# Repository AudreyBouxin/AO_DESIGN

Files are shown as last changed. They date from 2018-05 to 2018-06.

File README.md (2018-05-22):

# AO_DESIGN
Here are the codes and simulations for the design of the AO.

The Dimension code shows the calculations made to compute the OAP focal length and distances.

The Zemax file present the current status of the AO design.
The wavelength range is ???
The field of view is 1 arcmin (FoV/2 = 1/2x1/60=0.008333333°) before the dichroic and 8'' ((FoV/2 = 1/2x1/3600=0.00111111°) in the WFS path.

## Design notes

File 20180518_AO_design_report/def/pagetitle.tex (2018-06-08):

\setcounter{page}{1}
%\headsep          = 4.5cm
\fancyhf{}
\fancyhead[C]{
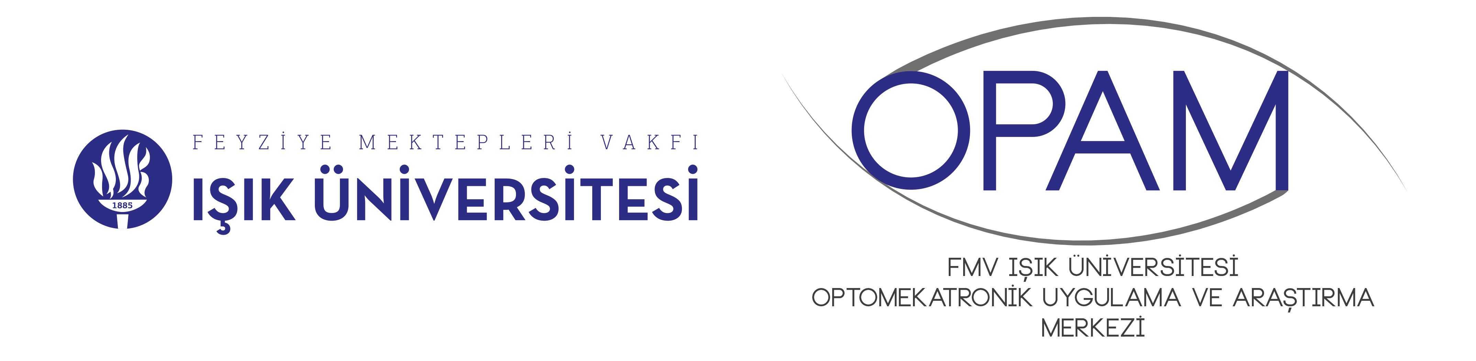
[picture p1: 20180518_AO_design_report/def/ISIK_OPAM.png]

{AO bench design}\hfill {\today}}
\phantom{bla}

\begin{center}
{\LARGE\textbf{AO bench design}} \\
\vspace{2mm}
{\LARGE\textbf{Zemax model and optimization}} \\
\vspace{2mm}
{\LARGE\textbf{post-PDR design}}\\
\end{center}

\begin{center}
\setlength\extrarowheight{20pt}
\begin{tabular}{p{2cm}p{3cm}p{4cm}p{3cm}}
 & Name & Date & Signature\\
Prepared &  A. Bouxin & \today & \begin{minipage}{.2\textwidth}
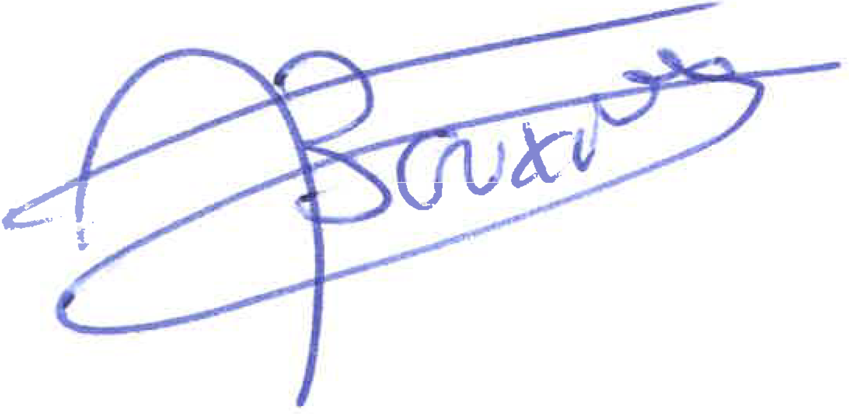
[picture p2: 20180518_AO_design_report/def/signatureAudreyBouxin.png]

\end{minipage} \\
Approved & L. Jolissaint & \today & \begin{minipage}{.2\textwidth}
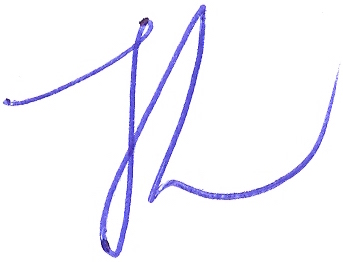
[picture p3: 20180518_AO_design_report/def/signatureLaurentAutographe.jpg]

\end{minipage} \\
& Name & October 10, 2017 & \dotfill \\
Released & Name & \today & \begin{minipage}{.2\textwidth}

\end{minipage} \\
& Name & \today & \dotfill \\
\end{tabular}
\end{center}

\lfoot{\vspace{5mm}}

%\phantom{bla}
\newpage

%\hspace{-0.6cm}
\begin{center}
\begin{tabular}{llcl}
Issue & Date & Sect./Page & Reason/Remarks \\ \hline
1.0 & Oct. 10, 2017 & All & New \\ \hline
2.0 & May 18, 2018 & All & Review of all the design after decisions and\\
	&				&	 &Paolo Spano advices \\ \hline
3.0 & June 08, 2018 & All & Review of all the design without the FCL\\ \hline
\end{tabular}
\end{center}
\newpage

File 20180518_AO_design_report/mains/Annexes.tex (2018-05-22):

\appendix

%\chapter{Codes Matlab d'acquisition des images}
%\section{Caméra Lumerea LU75}
%
%\subsection{Détermination de la répartition d'intensité du faisceau laser\label{ann:TLaserIntensityRepartition}}
%\lstinputlisting[language = MATLAB]{appendix/TLaserIntensityRepartition.m}
%\newpage

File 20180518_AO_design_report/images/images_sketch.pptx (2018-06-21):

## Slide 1

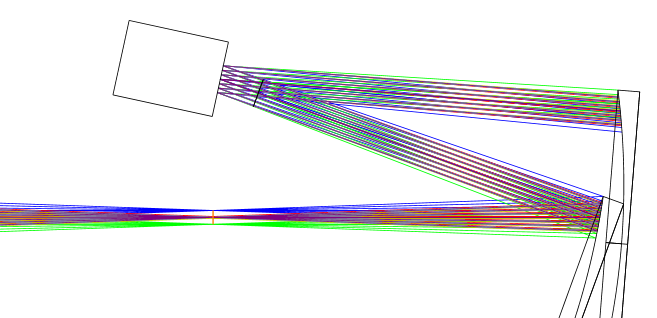
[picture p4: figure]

Début système AO

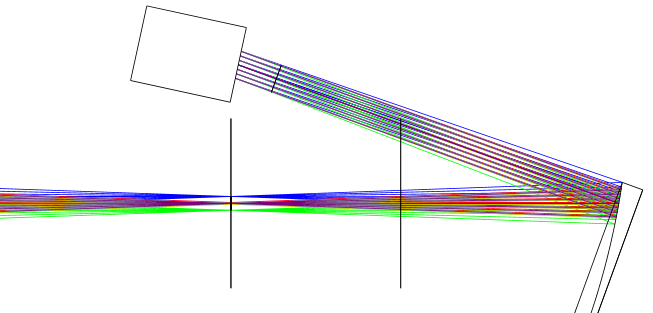
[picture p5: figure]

DM

DM

FoV

Telescope focal plane

Sketch 1

Telescope focal plane

200 mm

Sketch 2

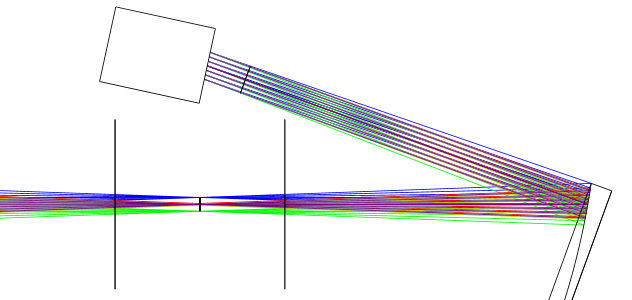
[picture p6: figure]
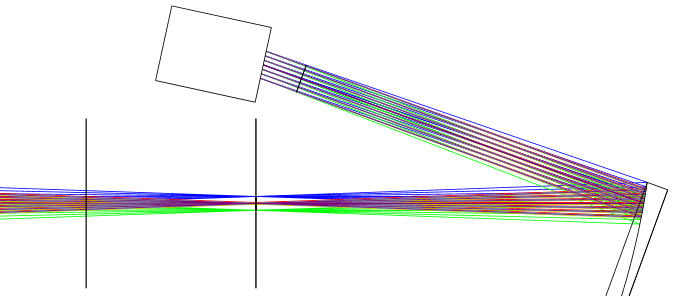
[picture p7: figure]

DM

DM

FoV

Telescope focal plane

FoV

Telescope focal plane

Sketch 4

Sketch 3

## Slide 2

DM

DM

FCL

Telescope focal plane

Sketch 1

Telescope focal plane

200 mm

Sketch 2

DM

DM

FCL

Telescope focal plane

FCL

Telescope focal plane

Sketch 4

Sketch 3

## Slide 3

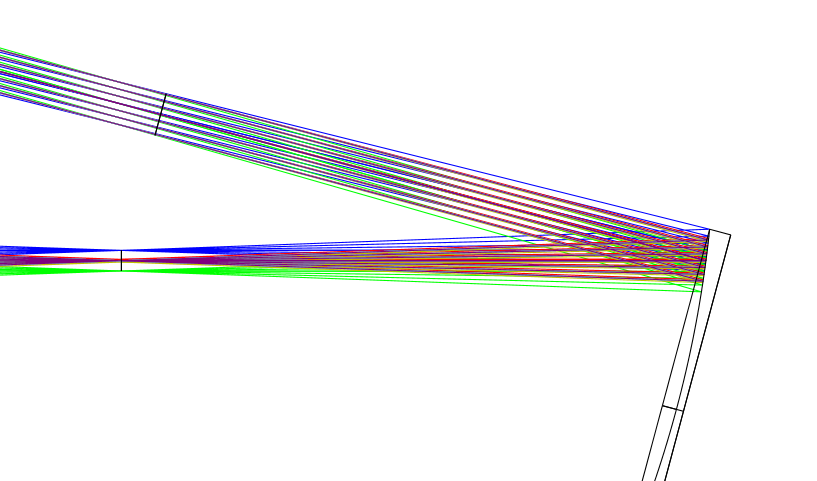
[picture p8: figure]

Pupil image

FCL

OAP0

θ= 15°

Telescope focal plane
(FoV = 1’)

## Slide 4

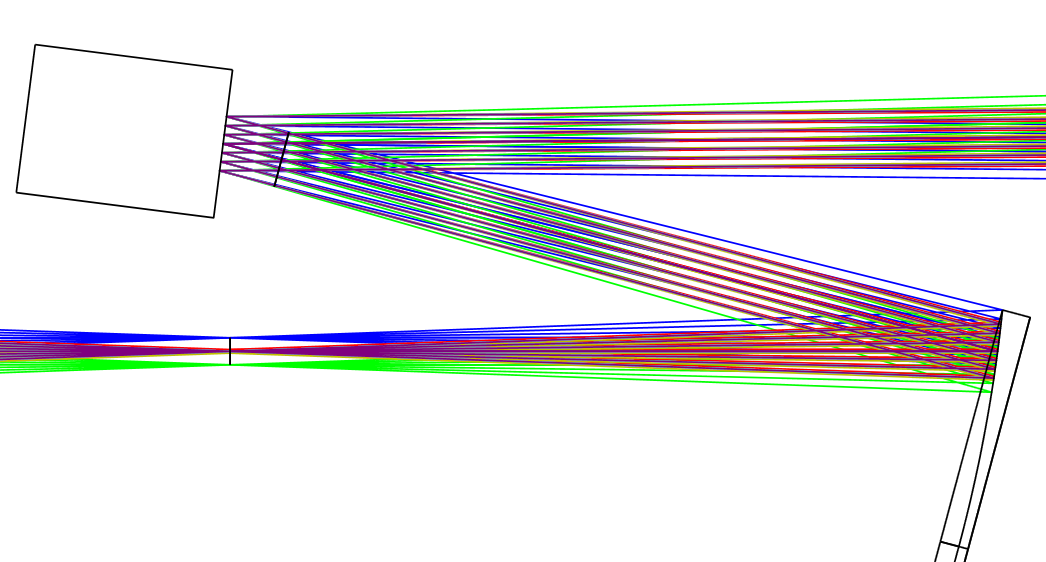
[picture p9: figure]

DM

2α

OAP0

θ= 15°

Telescope focal plane
(FoV = 1’)

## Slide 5

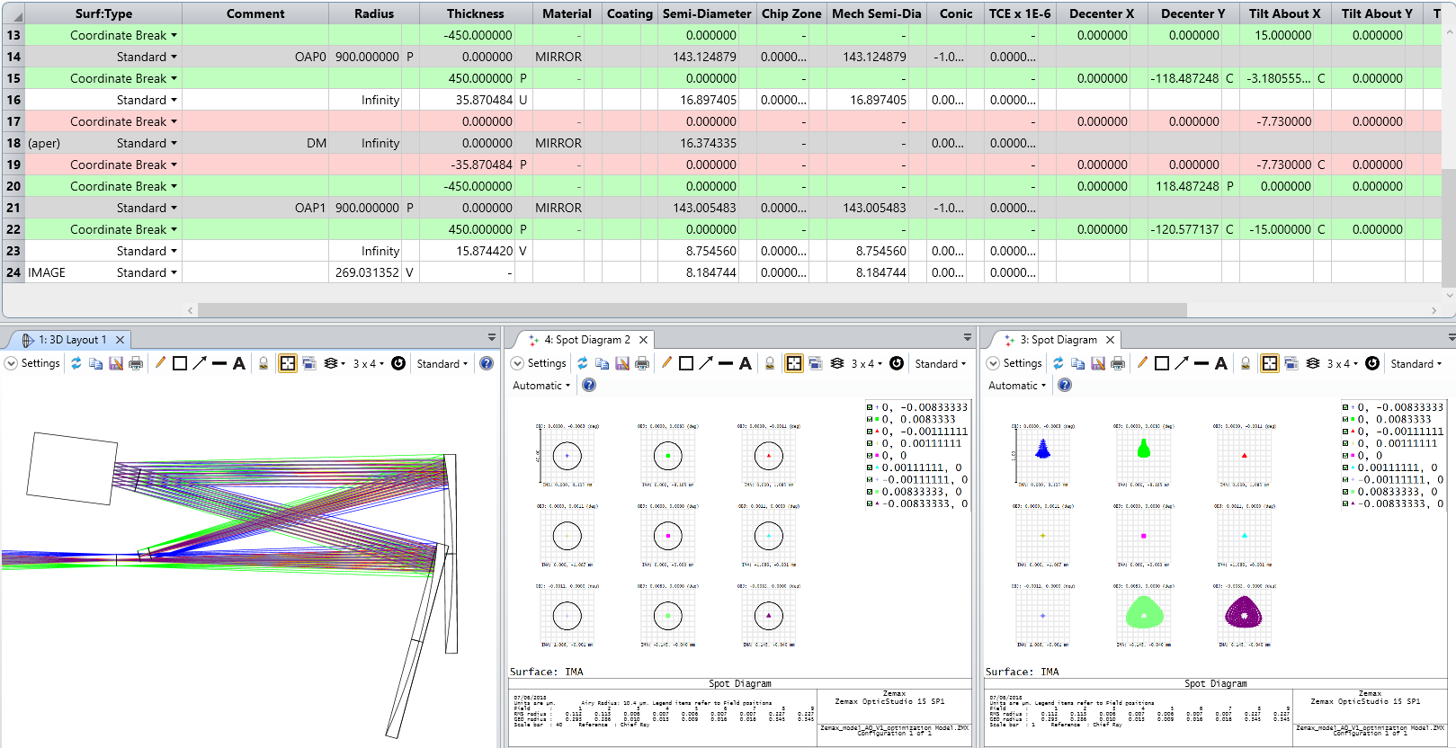
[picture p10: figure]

OAP1

DM

Telescope
focal plane
(FoV = 1’)

Intermediate
focal plane
(FoV = 1’)

≈

OAP0

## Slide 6

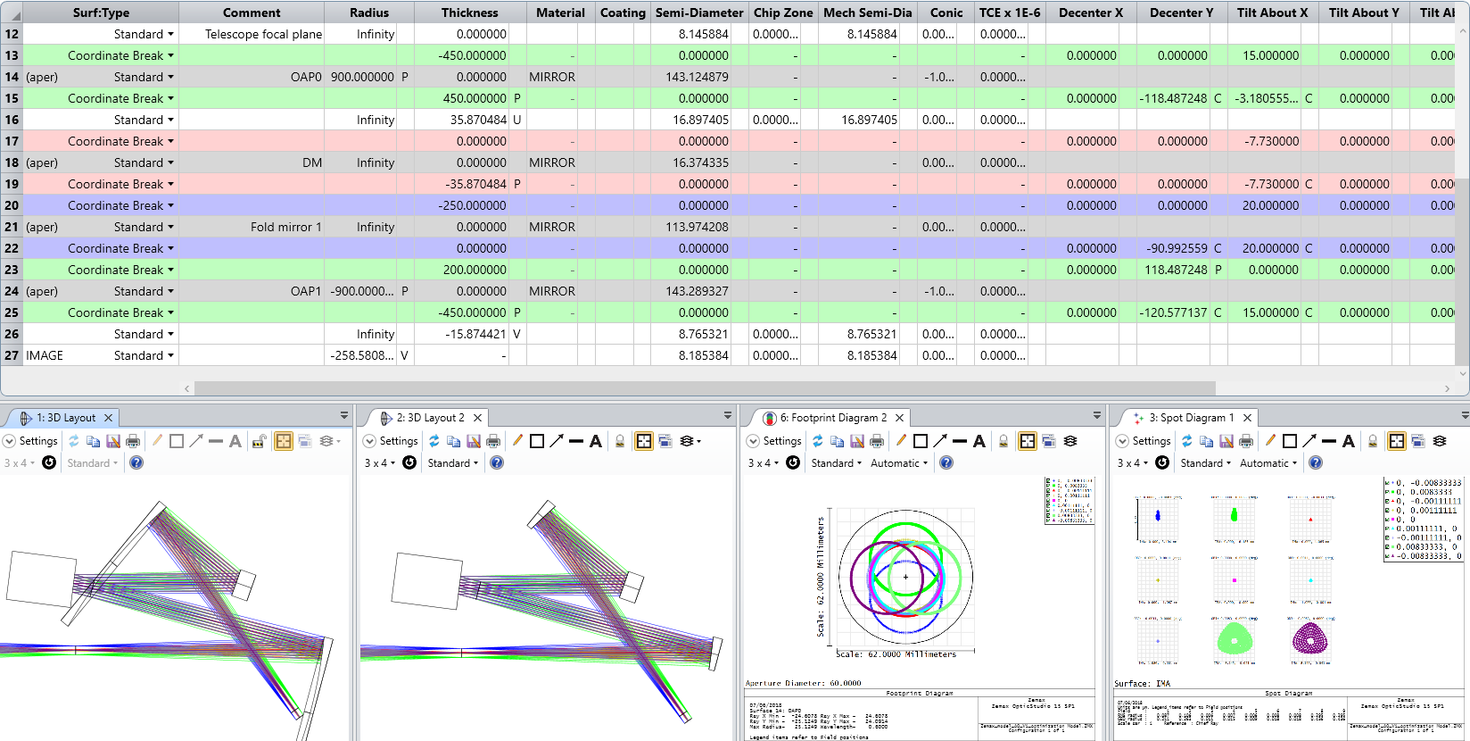
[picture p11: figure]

OAP1

OAP1

DM

Folding
mirror 1

OAP0

DM

Folding
mirror 1

OAP0

Telescope
focal plane
(FoV = 1’)

Telescope
focal plane
(FoV = 1’)

Intermediate
focal plane
(FoV = 1’)

Intermediate
focal plane
(FoV = 1’)

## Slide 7

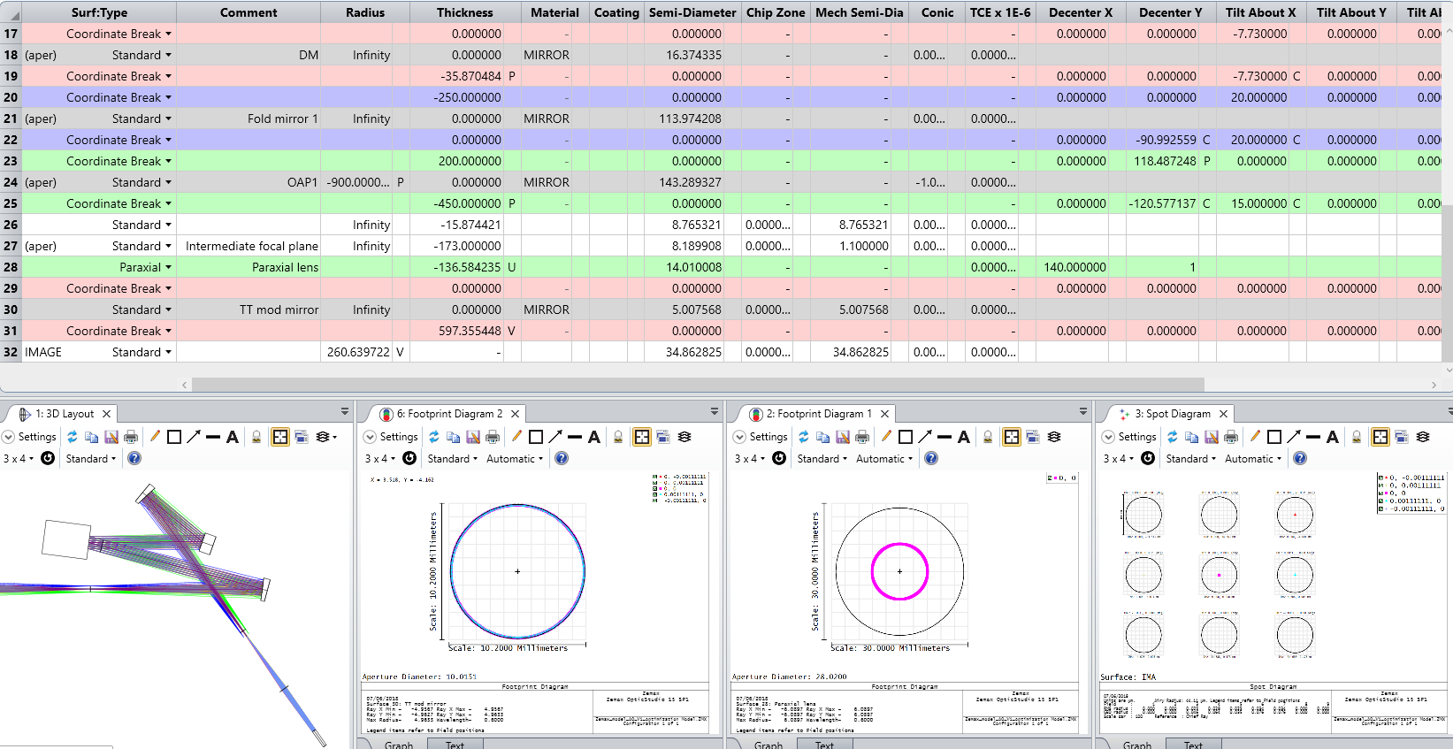
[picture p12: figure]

DM

OAP1

Folding
mirror 1

OAP0

Telescope
focal plane
(FoV = 1’)

Intermediate
focal plane
(FoV = 1’)

Paraxial lens

TT modulation
mirror

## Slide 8

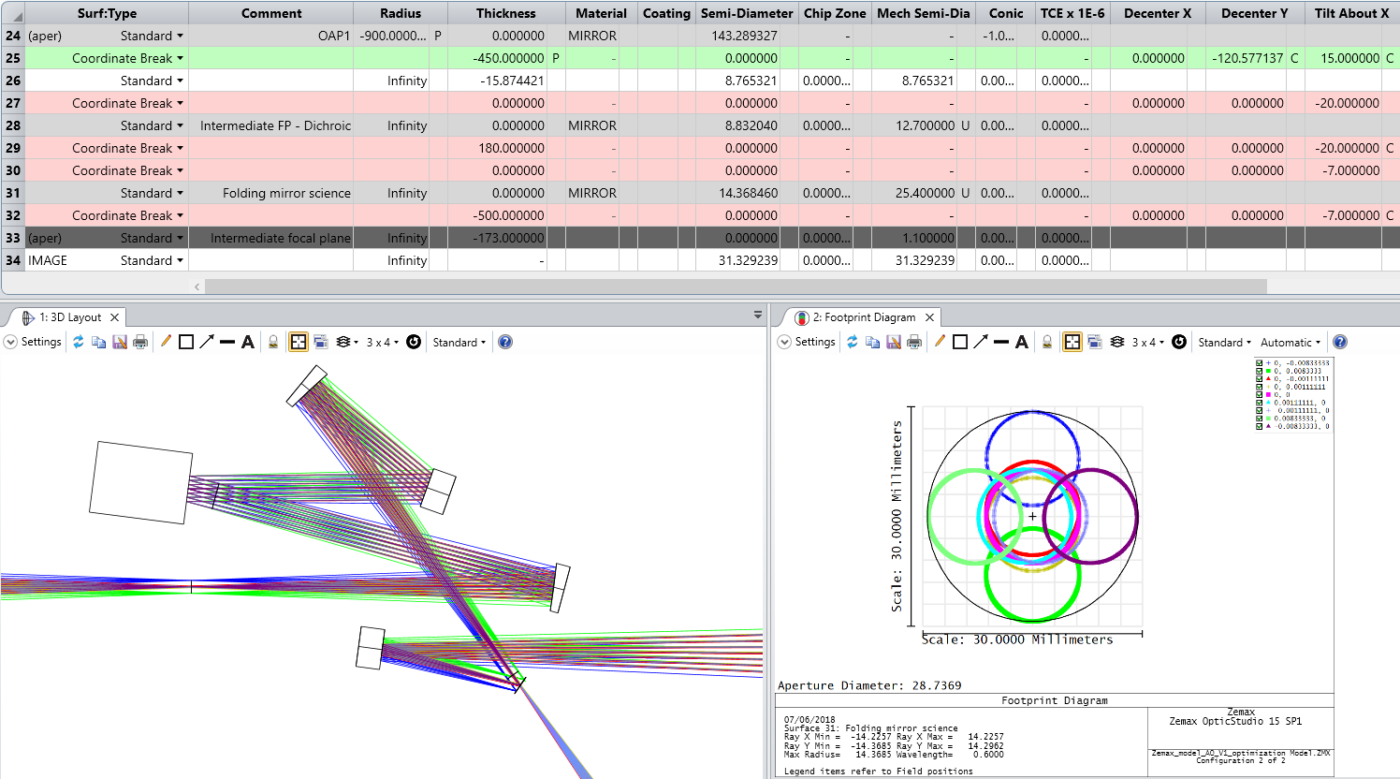
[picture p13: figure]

OAP1

DM

Folding
mirror 1

Telescope
focal plane
(FoV = 1’)

OAP0

Folding
mirror 2

Dichroic
membrane

≈

Intermediate
focal plane
(FoV = 1’)

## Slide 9

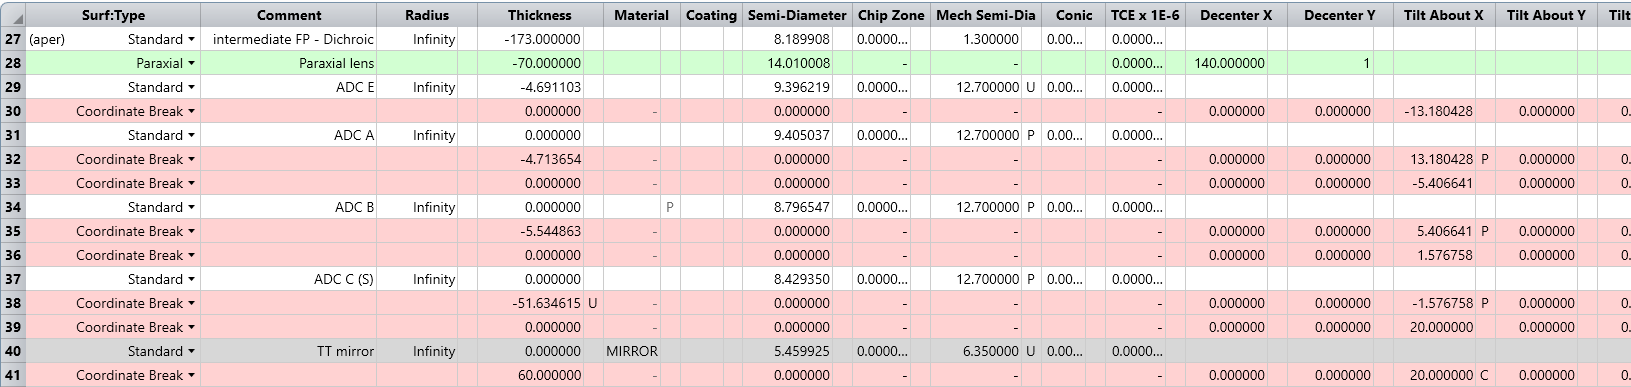
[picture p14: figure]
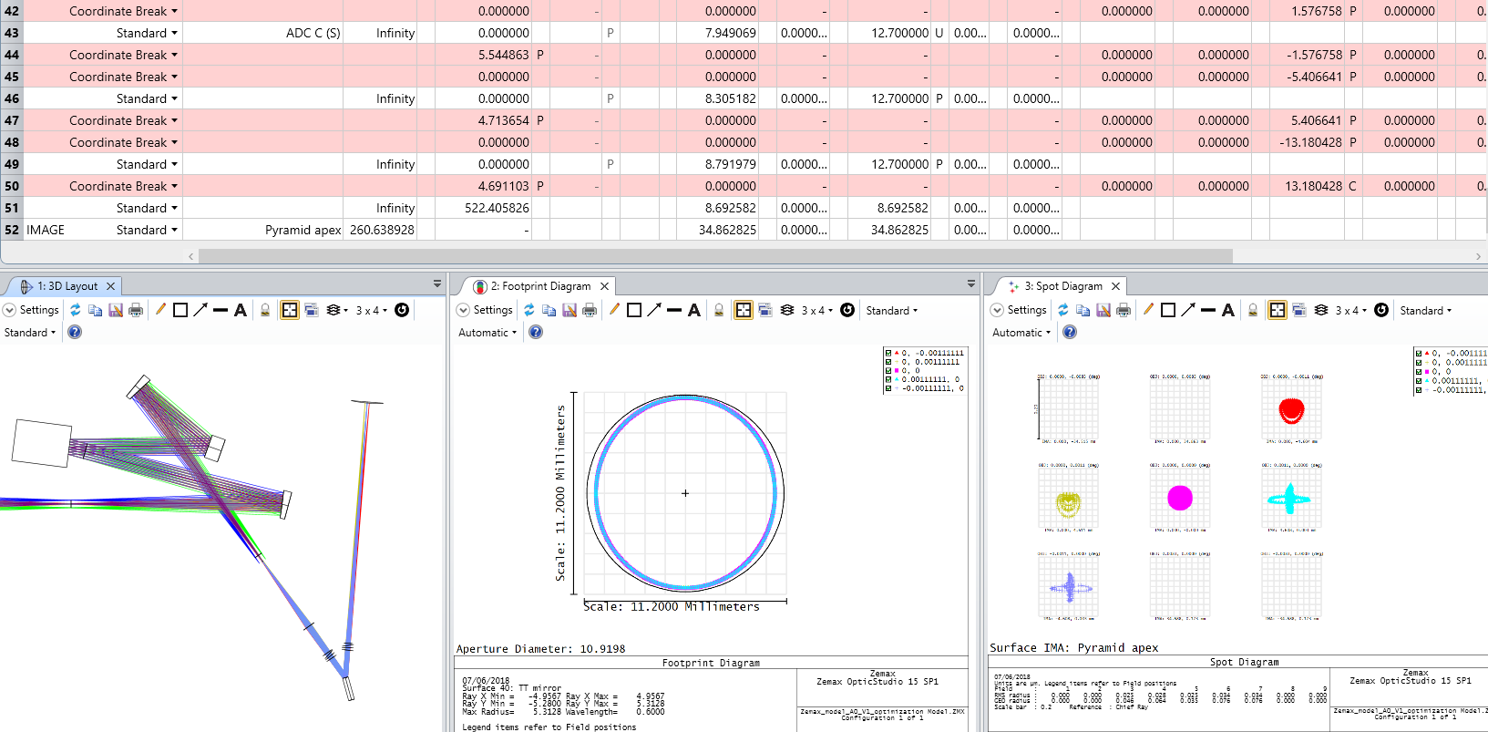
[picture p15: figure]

OAP1

Pyramid apex

DM

Folding
mirror 1

Telescope
focal plane
(FoV = 1’)

OAP0

Intermediate
focal plane
(FoV = 1’)

Paraxial lens

ADC
compound prism 1

TT modulation
mirror

ADC
compound prism 2

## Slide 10

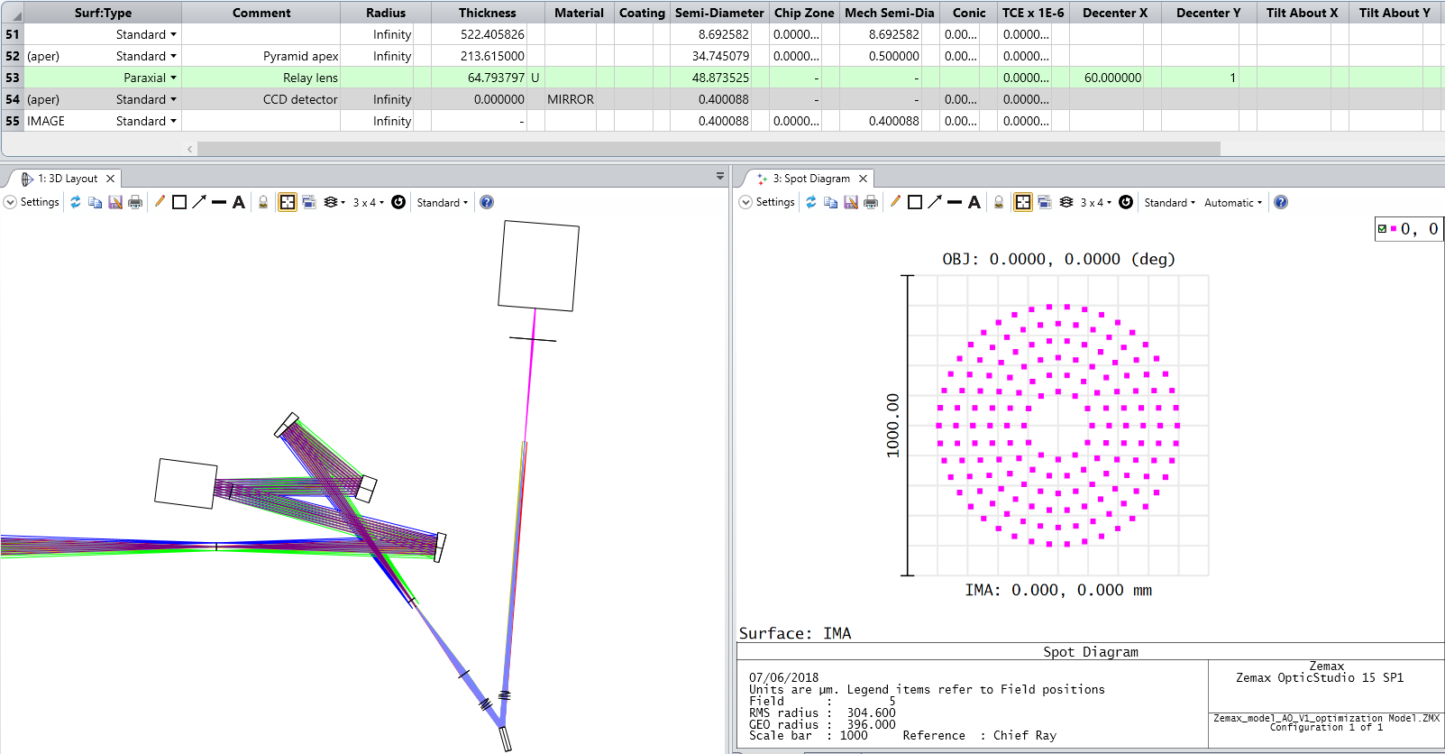
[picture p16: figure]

CCD
detector

Relay lens

OAP1

Pyramid apex

DM

Folding
mirror 1

Telescope
focal plane
(FoV = 1’)

OAP0

Intermediate
focal plane
(FoV = 1’)

Imaging lens

TT modulation
mirror

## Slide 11

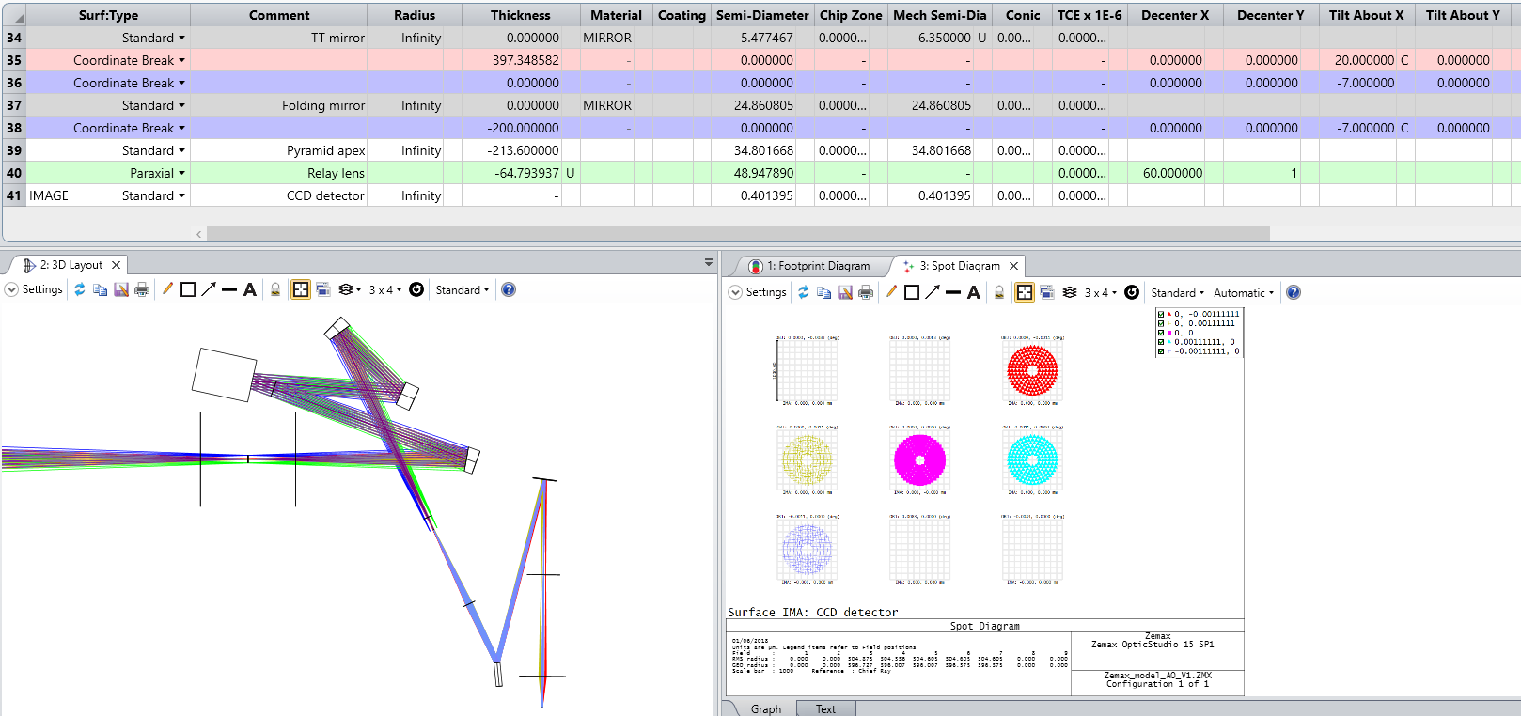
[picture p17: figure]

OAP1

DM

Folding
mirror 1

FCL

Telescope
focal plane
(FoV = 1’)

OAP0

Folding
mirror 2

Intermediate
focal plane
(FoV = 1’)

Paraxial lens

TT modulation
mirror

Pyramid apex

CCD detector

Relay lens

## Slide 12

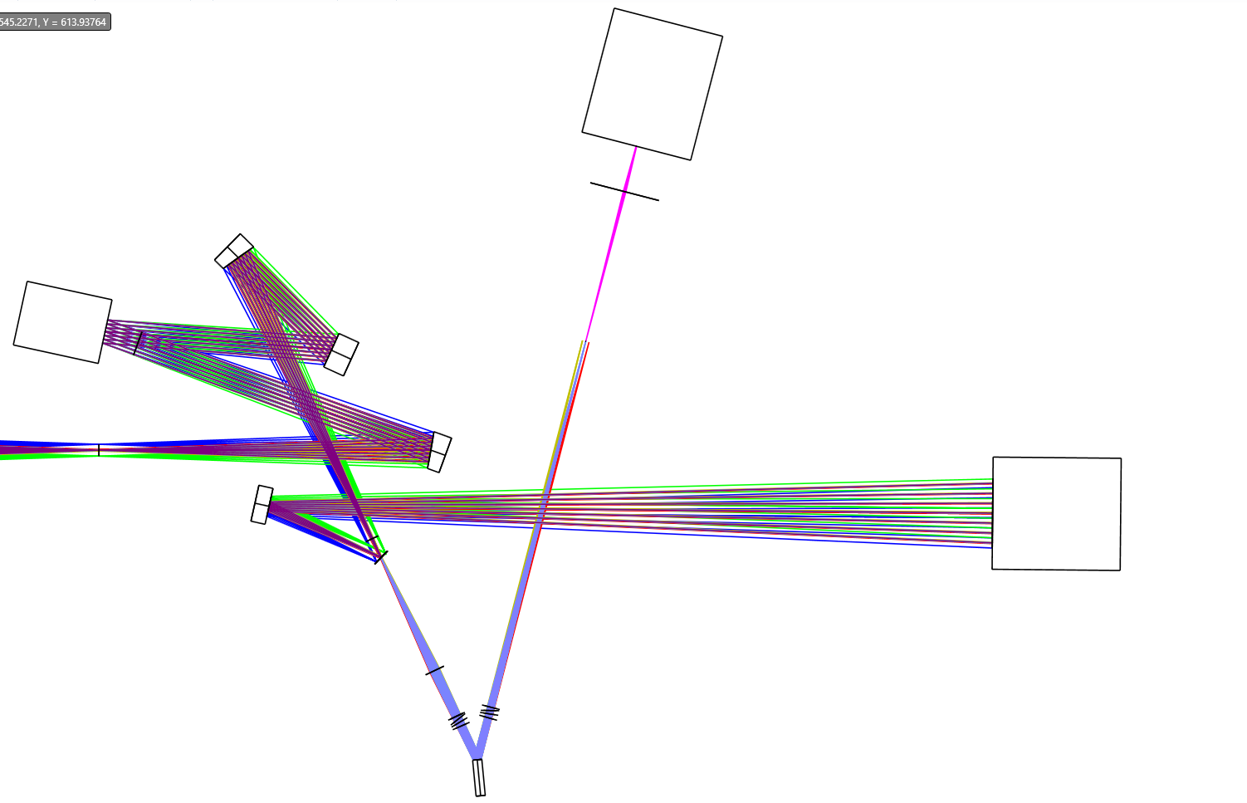
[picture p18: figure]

CCD
detector

Relay lens

OAP1

DM

Folding
mirror 1

Pyramid prisms

Telescope
focal plane
(FoV = 1’)

OAP0

To science

Folding
mirror 2

Dichroic mirror
@Intermediate
focal plane
(FoV = 1’)

Imaging lens

ADC
compound prism 1

ADC
compound prism 2

TT modulation
mirror

1 m

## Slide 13

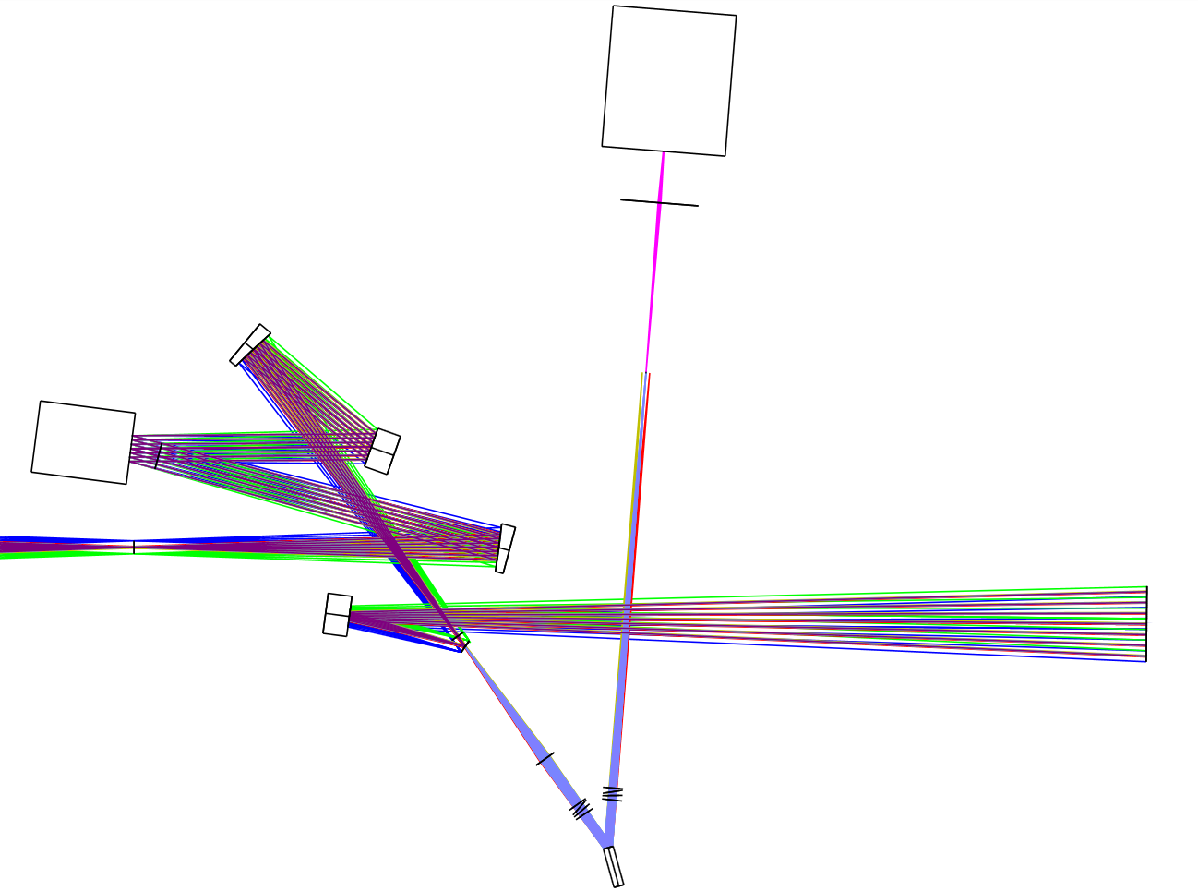
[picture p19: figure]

CCD
detector

Pyramid prisms

Relay lens

OAP1

DM

Folding
mirror 1

OAP0

Telescope
focal plane
(FoV = 1’)

Folding
mirror 2

To science

Dichroic mirror
@Intermediate
focal plane
(FoV = 1’)

Imaging lens

ADC
compound prism 1

ADC
compound prism 2

1 m

TT modulation
mirror

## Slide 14

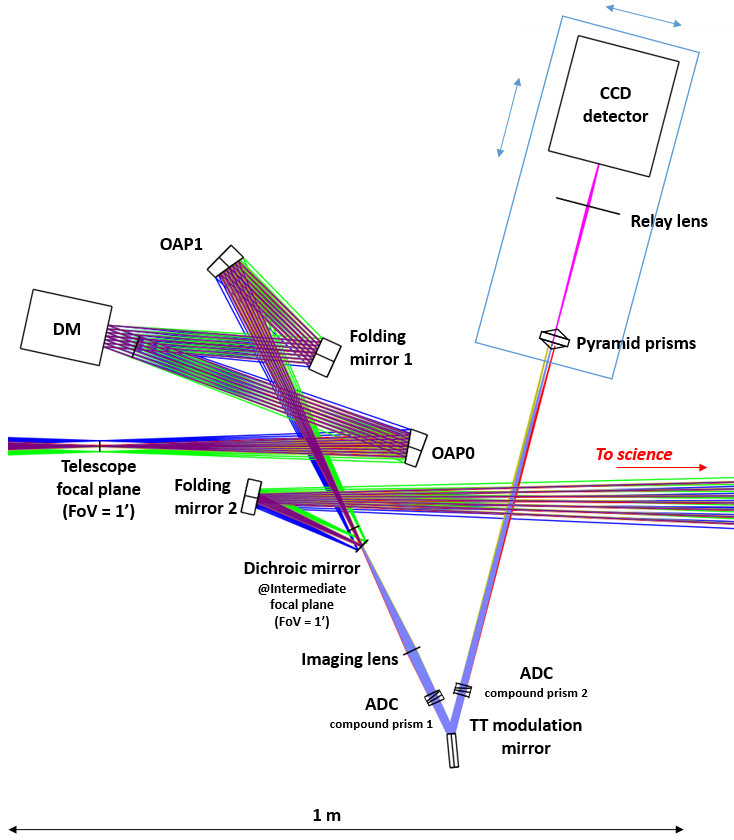
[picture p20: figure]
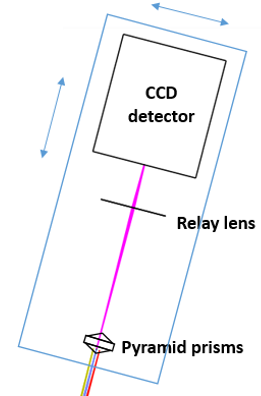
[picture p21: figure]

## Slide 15

θA

θB

θB

θA

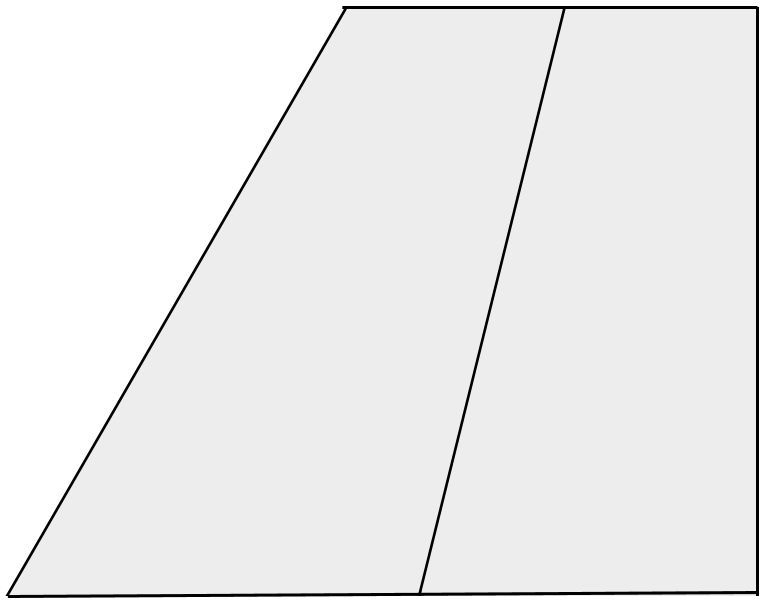
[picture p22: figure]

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
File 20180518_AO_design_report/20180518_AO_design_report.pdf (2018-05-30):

AO bench design | May 30, 2018

## AO bench design Zemax model and optimization post-PDR design

Name | Date | Signature
Prepared | A. Bouxin | May 30, 2018
Approved | L. Jolissaint | May 30, 2018
Name | October 10, 2017 | |
Released | Name | May 30, 2018
Name | May 30, 2018 | |

AO bench design | May 30, 2018
Issue Date | Section/Page affected Reason/Remarks
1.0 | October 10, 2017 | All | New
2.0 | May 18, 2018 | All | Review of all the design after decisions and Paolo Spano advices

AO bench design | May 30, 2018

## Acronyms

aO | active Optics
AO | Adaptive Optics
CCD | Charge Coupled Device
CMOS | Complementary Metal Oxide
Semiconductor
DAG | Dogu | Anadolu | Gozlemevi
(East Anatolian Observatory)
DM | Deformable Mirror
FCL | Field Correction Lens
FoV | Field-of-View
FWHM | Full Width at Half Maximum
NCPA | Non Common Path Aberra-
| tions
NGS | Natural Guide Star
OTF | Optical Transfer Function
P2V | Peak-to-Valley
PSF | Point Spread Function
PSF-R | PSF Reconstruction
PWFS | Pyramid WFS
RMS | Root Mean Square
SH-WFS | Shack-Hartmann WFS
SNR | Signal-to-Noise Ratio
TT | Tip-Tilt
WFS | Wavefront Sensor
WFE | Wavefront Error

AO bench design | May 30, 2018

## 1 Scope of this document

This document presents the DAG adaptive optics (AO) optical train design and optimization.

## 2 Introduction

There are several mandatory points we have to handle :

- the exit pupil has to be imaged on the DM;
- the DM diameter is fixed to the DM-468 from ALPAO; that means 33 mm;
- the exits pupil has to be imaged on the TT mirror for the P-WFS modulation;
- the beam has to converge on the pyramid apex;
- the angle of the beam that arrives onto the pyramid apex is calculated in order to get a diffraction limited PSF size of 2 times the pyramid roof;
- the exit pupil has to be imaged onto the EMCCD detector
- the beam footprint diameter onto the detector has to be defined accordingly to the oversampling criterion (explained section 3.3).

We use off axis parabolas (OAPs) for all our design to reduce the aberrations (compared to lenses). We have added one more constraint on the design which is to have parallel beam arriving or leaving each off axis parabola in order to limit the spherical aberrations.

The fixed parameters are resumed here :

- exit pupil diameter : ExtP = 727.4046 mm;
- distance exit pupil to focal plane : ExP-FP = 10338.74 mm;
- DM diameter : DM = 33.0 mm;
- pixel size of the Nuvuu EMCCD AO : PxSize = 24 µm

AO bench design | May 30, 2018

In order to design the AO bench we started with the telescope model. Indeed, we would try to compensate for the field of curvature introduced by the mirrors of the telescope with the off-axis parabolas (OAP) of the AO. The Zemax model of the telescope shows a curvature radius of about 1255 mm.

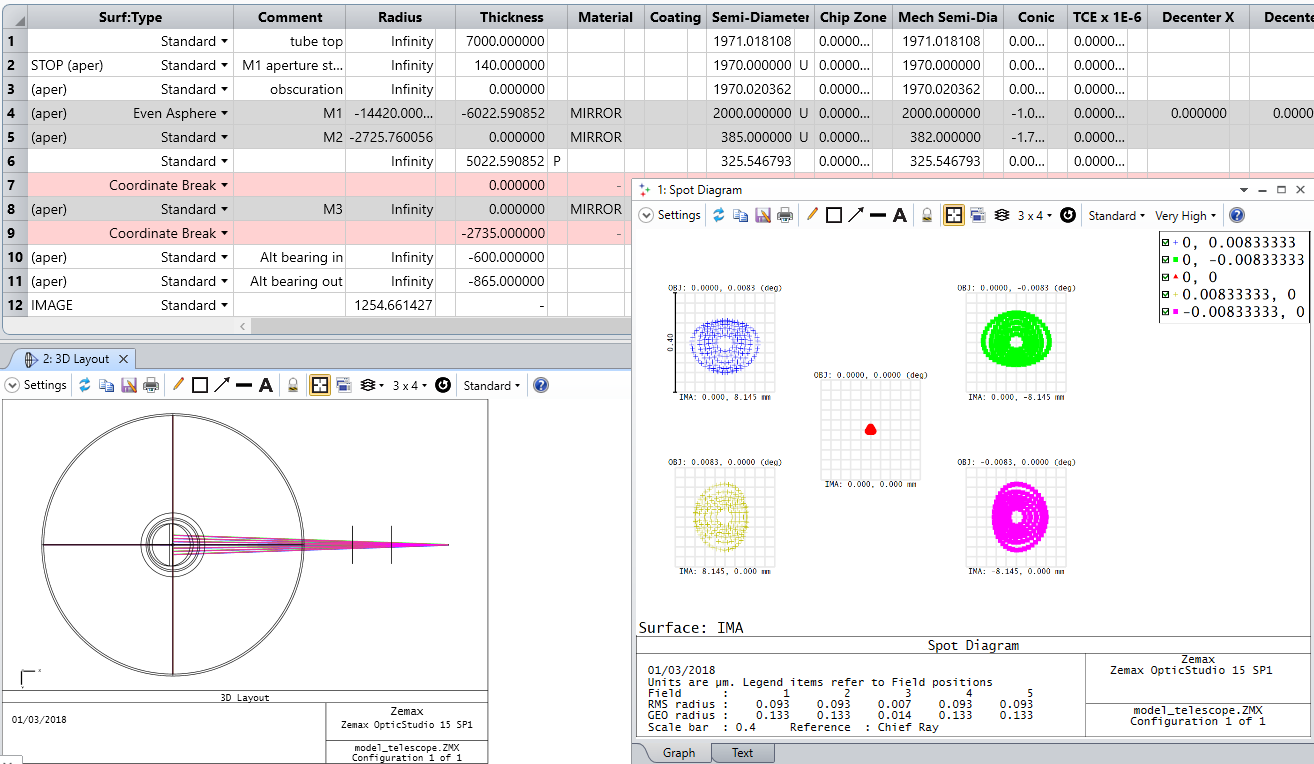
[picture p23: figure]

Figure 1: Zemax model of the telescope

AO bench design | May 30, 2018

## 3 Design development and optimization

A preliminary design have been set for the PDR and the main points are summarized at each optimization step of this report.

### 3.1 Imaging the exit pupil of the telescope onto the DM

The first branch consists on an imaging system of the telescope pupil onto the DM. The beam has to be collimated and the footprint has to take the entire clear aperture of the DM (for the DM-468 from ALPAO DM = 33 mm).
The beam on the DM has to be reflected with a certain angle otherwise the reflected beam comes back on itself. The maximum acceptable angle can be calculated considering the position error of the beam per actuator on the DM. We can align the beam with an error of 1/10thΛ (Λ the actuator pitch = 1.5 mm for the ALPAO DM-468). In order for the projected beam diameter to be no more than 10% smaller than the DM diameter on both side, the tilt of the DM must be no more than α (figure 2) :

α = arccos

1 −

1
5

Λ

DM !

α = arccos
1 −

1
5

1.5
33

α = 7.73◦
(1)
2α = 15.46◦

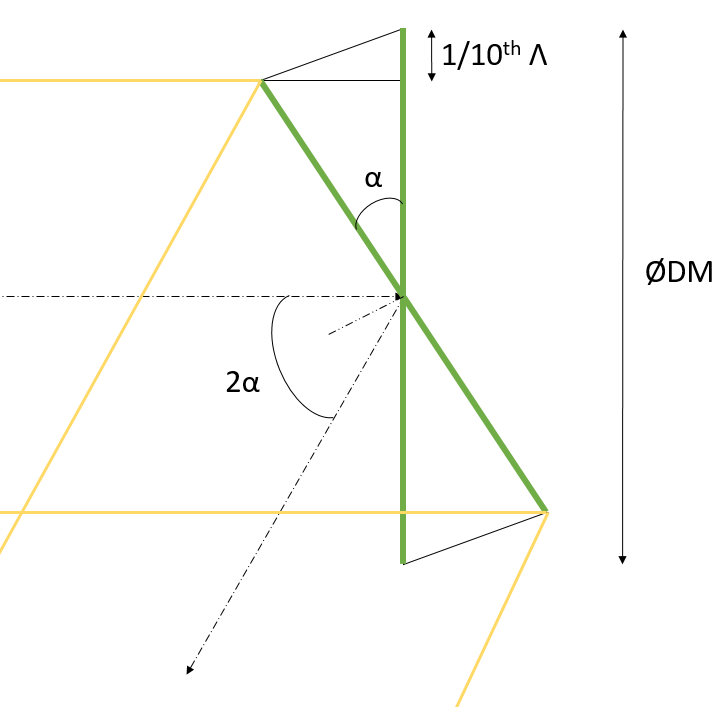
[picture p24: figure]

Figure 2: Sketch of the input and output beam depending on the tilt angle of the DM

AO bench design | May 30, 2018

The input beam diameter is then :

DM-beam = DM cos α = 33 × cos (7.73) = 32.7 mm | (2)

In order to have a collimated beam on the DM with a diameter of DM-beam, the focal length of the OAP0 is calculated by the following sequence of equations. To visualize the parameters needed and the context we can look at figure 3. The with an angle θ with the corresponding reference coordinates (0, x⁰

, y⁰
). The ray ∆CR corresponds to the chief ray, ∆αu is the ”upper” marginal ray and ∆αb is the ”bottom” marginal ray. The origin is placed at the focal plane of the telescope.


Figure 3: Ray tracing of a tilted parabola

In the reference coordinates (0, x⁰

, y⁰
), we have (with PFL the Parental Focal Length of the OAP):
- equation of the parabola θ :

y

0 =

x

02
4 PFL
− PFL | (3)
- equation of ∆αu :
y

0 = −

1
tan (θ + α)

x

0
| (4)

AO bench design | May 30, 2018
- equation of ∆αb :
y

0 = −

1
tan (θ − α)

x

0
(5)

Determination of x

0
Exθ u (intersection between parabola θ and ∆αu) :
(3) = (4)

x

0
Exθ u = 2 PFL

−

1
tan (θ + α)

+

s
1
tan²
(θ + α)

+ 1!
(6)

Determination of x

0
Exθ b (intersection between parabola θ and ∆αb) :
(3) = (5)

x

0
Exθ b = 2 PFL

−

1
tan (θ − α)

+

s
1
tan²
(θ − α)

+ 1!
(7)

In order to have the OAP0 output beam diameter equal to the DM clear aperture we have :

x

0
Exθ u − x

0
Exθ b = DM-beam | (8)

The parental focal length (see appendix A) of OAP0 is :

PFL = 1
2

DM-beam
−

1
tan(θ+α) +

q 1
tan²(θ+α) + 1 + 1
tan(θ−α) −

q 1
tan²(θ−α) + 1

(9)

Using the equation (24) described in appendix A we can transform the parental focal length into the effective focal length.

For the OAP0 the angle αOAP0 is

αOAP0 = arctan ExP/2
ExP-FP
(10)

The numerical application of (10) with ExP = 727.4046 mm and ExP-FP = 10338.74 mm gives αOAP0 = 2.015°, the aperture demi angle of the beam arriving on the first OAP.

After the discussion we had with Paolo Spano, we took his advice into account and choose the parabola tilt angle according to the following precept : θ = 35° is a critical choice and θ > 35° is a nightmare (manufacturing and alignment). We should take an tilt angle

AO bench design | May 30, 2018

smaller than 30° to be realistic and the smaller the best. However, we are limited by the space around the focal plane because of the field correction lens (represented by the bloc on figure 4). Depending on where it is going to be placed we would have to increase the

angle of OAP0. An email has been sent to AMOS who is going to design the FCL to know if it is possible to have it before the focal plane.


Figure 4: Field correction lens position from the focal plane of the telescope

We can set the parabola tilt angle to θ = 20° in order to keep this angle as small as possible to limit aberrations.

Using these inputs the focal length of the OAP0 is (appendix D): PFLOAP0 = 443.13 mm. This value is too specific so we round it to¹
:

PFLOAP0 = 445 mm

1
In Zemax, we enter the PFLOAP0 and not the effective focal length in the coordinate break surface because using it, the translation is done before the tilt angle. This is why if we enter the translation in a surface before the coordinate break we cannot use the same length (we would then write the EFLOAP0)

AO bench design | May 30, 2018

The image of the exit pupil given by OAP0 gives the position of the DM. Its position pi relative to the OAP0 vertex is given by (we use Gauss law) :

pi | = po PFLOAP0 po + PFLOAP0 | (11)
pi | = −(10338.74 + 445)445 −10338.74 | (12)
pi | = 464 mm | (13)

The Zemax ”pick up pupil position” macro is used to get the perfect DM position wrt the OAP0. The DM is then at pi = 493.08 mm. Even if we understand that we cannot align the DM reflecting surface with this accuracy, we keep it in the Zemax model and we will work on that during the tolerancing analysis²
The image of the pupil through a tilted OAP is also tilted (see [1]). This creates pupil aberrations.


Figure 5: Tilted image of the pupil

Here we want to place the DM at this pupil position. When we work with OAPs the image stop after an OAP is not perpendicular to the optical axis. The OAP introduce a tilt angle

2We always keep all the digit during an AO design in order to see what are the best results we can obtain with an ideal system.

AO bench design | May 30, 2018

of the image plane. If we tilt the DM in the opposite position of this OAP-introduced tilt angle we add pupil aberrations whereas if we tilt it the same direction we can compensate for it.

(b) Zemax footprint diagram of the beam

(a) Layout
on the DM

Figure 6: Zemax model of the 1rst part of the AO design

The beam footprint on the DM shows that all the field fits inside the clear aperture. The maximum diameter is equal to 32.7306 mm (< 33 mm). The angle of the DM is set to -7.73° (equation (1)),and not 7.73°as explain above.

### 3.2 Imaging the pupil on the TT modulation mirror

### 3.2.1 Create an image of the pupil

We need to image the pupil on the TT modulation mirror. Moreover, we know that to compensate for the introduced aberration from OAP0 we can use an OAP1 with the same focal length. The F/D ratio would stay the same as the telescope one which is favourable for the science path.
Figure 7 shows that to model this combination we use the ”chief ray” solve on Zemax (Lens data) to keep the coordinates following the beam path (using the on-axis ray). OAP1 is placed at the exact inverse position of OAP0 in order to compensate for its aberrations so the intermediate focal plane is near the telescope focal plane.

AO bench design | May 30, 2018


Figure 7: Zemax model from the telescope beam to the intermediate focal plane

We use an optimization (smallest spot radius) to go to the best focal plane (surface # 76 thickness is set as variable) and in order to consider the field curvature we set the radius of the image plane variable. The optimization using a merit function (Type : P2V, Crite-ria : Spot Radius, Reference : Chief Ray) is done on the image surface to get the smallest spot radius of the central beam (FoV = 0’). We can see that the spot diameter varies between 0.511 µm and 0.009 µm (the center of the FoV) but when we look the spots with the Airy disk we can say that the beam is well focused.
However, the radius of the image curvature is smaller than the telescope output field of curvature so we did not compensate for that, instead we increase it (we will see how we could work on that or not).

### 3.2.2 Bend the beam

We do not want the beam to go back in the field correction lens and we would like to place the dichroic nearby the intermediate focal plane. In order to do that properly, we fold the beam after the DM with a flat mirror.

AO bench design | May 30, 2018


Figure 8: Zemax model from the telescope beam to the intermediate focal plane with a fold mirror after the DM

Figure 8 shows the new design with a folding mirror tilted at 20°. For more clarity we apply the real aperture size of the OAPs on layout 1. We can see on the footprint diagram that we can use two OAPs of 2 inches of diameter. The maximum diameter of the beam footprint (for a FoV = 1’) is about 49.9 mm. However, we should be careful and verify during the tolerance analysis that when we move the OAP in the alignment precision range we can do, the entire beam stays reflected on the OAP (no vignetting). Concerning the folding mirror, we can also use a diameter of 2 inches it is positioned at 298 mm from the DM (same as above, we have to check during the tolerancing that we do not have vignetting when moving around this position).

After redoing the optimization of the intermediate focal plane position and the image radius of curvature we found spot diameters vary from 0.009 µm (on-axis) to 0.603 µm (0.5’) across the FoV (see figure 9).

AO bench design | May 30, 2018


Figure 9: Spot diagram at the intermediate focal plane for the AO FoV and the WFS path FoV

### 3.2.3 Imaging the pupil on the TT modulation mirror

The | selection | of | the | star | in | the | FoV | is | made | using | an | XY | stage | where | all | the | WFS | path
would | be | mounted | (as | we | have | a | compact | WFS | path). | Now, as the OAP0 and OAP1 are
the same, this optical configuration creates an image of the pupil of the same diameter at
the same distance from the FP as the entrance pupil.
It is so not possible to use it to place the TT modulation mirror which has to be about
10 mm in diameter and at a reasonable distance from FP. FOR these reasons |
we | take | a | TT | modulation | mirror | of 0.5 | inch | mounted | on | the | fast | tip-tilt | platform | S-331
from | PI. | We want to have a beam of about 10 mm in diameter at the pupil to place the
TT stage.

We have also to note that we would like to introduce a dichroic membrane nearby the intermediate focal plane.
We know that we need to arrive on the pyramid roof (P-WFS) with a corresponding :

F # = 2pyramid roof
| | | | | | | | | | λ | | | | | | | | (14)

Taking a pyramid roof of about 20 µm according to Jean-Pierre Veran (private communi-cation) at λ = 0.6 µm we have :
F # = 66.7 | (15)

AO bench design | May 30, 2018

We round this value to F# = 60 (we need to investigate the pyramid roof size that can be manufactured).

We want then a vergence that takes the beam with a F# of 14 and brings it to 60. The TT modulation mirror is placed in this converging beam at the pupil position. At first approximation, we can do a geometrical dimensioning. We use a drawing software and apply the constraints to calculate which focal length and distance from the intermediate focal plane we need. In order to build this ray tracing properly we calculate the following parameters :

F #input =

ExP-FP

ExtP

F #output =

flens

beam on the lens

γinput =

1

2F #input

γoutput =

1

2F #output

The image of the pupil is nearby the foci (at 0.06 mm) and has to be about 5 mm in diameter. Taking the angles and the beam diameter on the TT modulation mirror we find the focal length of the lens and the distance from the intermediate focal plane described figure 10.


Figure 10: Ray tracing using SolidWorks to approximate the converging lens before the TT modulation mirror

AO bench design | May 30, 2018

We introduce these results in Zemax using a paraxial lens (figure 11). We can see that the beam diameter is about 5 mm as expected.


Figure 11: Zemax model from the telescope beam to the TT modulation mirror using a paraxial lens

We want to tilt the TT modulation mirror to send the beam in a convenient direction. We need to add the ADC nearby a pupil plane, so if we want to use the pupil where the TT modulation mirror is placed we need some space around it to insert the ADC. We can tilt the TT modulation mirror with an angle of about 20°. The radius of the beam footprint on the TT modulation mirror measured on the Zemax model is 5.32 mm at maximum (which is smaller than 0.5 inch).
Moreover, the focal length of 142 mm is not a common value so we can change it to 140 mm.

We use the optimization tool to find the best focal plane (distance and radius of curvature at the image plane). As we are going to move all the WFS path with a XY stage to pick up the star, we can determine the beam footprint diameter on the paraxial lens with the on-axis case. We can see that the F# of the beam arriving on the apex of the pyramid

AO bench design | May 30, 2018

(figure 11) is F# = 136.59+579.88
7.1884∗2 = 58.5 which is smaller than the F#fixed before at 60. We can adjust it moving a little bit the paraxial lens from the intermediate focal plane. We find the final solution (figure 12) with F# = 136.59+597.35
6.0897∗2 = 60.3.


Figure 12: Zemax model from the telescope beam to the apex of the pyramid WFS.

Actually, | we | could | play | with | the | angle | of | the | TT | modulation | mirror | to | place | the | ADC
closer | to | the | pupil | plane. | This | would | be | investigate | according | to | the | ADC | design.

### 3.3 Image the pupil on the CCD detector

The detector is the Nuvuu EMCCD with 128 pixels and a pixel size of 24 µ m. We have to sample the beam with at least 1 pixel per actuator. In order to relax the alignment problems we can oversample the beam. According to Jean-Pierre Veran advice an oversampling of 1.5 should be enough. The ALAPO DM-468 has 22 actuators across the clear aperture diameter (so 23 pitches). Then we can calculate the beam diameter on the detector :

CCD | = #actuator across × PxSize × Oversampling factor | (16)
CCD | = 22 × 24 µm × 1.5 | (17)
CCD | = 0.792 mm | (18)

AO bench design | May 30, 2018

The pupil has to be images on the camera. The TT mirror (pupil plane) image through the OAP3 is at the infinity. So when we image it through the relay lens the pupil plane arrives at the focal plane of the relay lens. Moreover, in order to get the beam size on the camera, the focal length of the relay lens (fLR, see appendix B) has to be :

fLR | = F# × CCD | (19)
fLR | = 60.26 × 0.792 | (20)
fLR | = 47.73 mm | (21)

surface 26 thickness variable : jouer avec cette valeur pour obtenir un diametre de 0.792mm
sur | la | CCD | = | 0.396mm | en | rayon

STOOOOOOOOOOOOOOOOOOOOOOOOOOOOOOOPPPPPPPPPPPPPPPPP The remaining optics have been implemented in the Zemax model just to have an estima-tion of the space no optimization has been done (we can already see that the diameter is not precisely of CCD).


Figure 13: Zemax model of the bench until the CCD camera

AO bench design | May 30, 2018

### 3.4 Atmopsheric Dispersion Compensator (ADC)

We are designing an ADC to compensate the atmospheric dispersion (see appendixC). The geometric parameters and the glass are not set yet this is why we do not have implemented it in the Zemax model for now. However, we can already say that the ADC would probably be inserted between OAP2 and OAP3 because the beam is collimated.

AO bench design | May 30, 2018

## References

[1] R. M. Malone, D. Dolan, G. Stevens, and W. Turley, “Design of a thermal imaging diagnostic using 90 degree off-axis parabolic mirrors,” Proceedings of SPIE, 2006.
[2] D. Kopon, L. M. Close, and V. Gasho, “An advanced atmospheric dispersion corrector: the magellan visible ao camera,” tech. rep., University of Arizona, 2012.
[3] C. Wynne, “A new form of atmospheric dispersion corrector,” Monthly Notices of the Royal Astronomical Society, no. 262, pp. 741–748, 1992.
[4] P. Ciddor, “Refractive index of air: new equations for the visible and near infrared,” Applied Optics, vol. 35, no. 9, 1996.
[5] W. . V. de la pression atmospherique avec l’altitude.
[6] Davis, “Equation for the determination of the density of moist air (1981/91),” tech. rep., Metrologia, 1992.

[7]

[8] R. C. Stone, “An accurate method for computing atmospheric refraction,” Astronom-

ical Society of the Pacific, 1996.

[9] R. C. Stone, “A new method for computing differential color refraction,” The Astro-

nomical Society of the Pacific, 2002.

[10] S. Tendulkar, Beyond the Blur: Construction and Characterization of the First Au-

tonomous AO System and an AOs urvey of Magnetar Proper Motion. PhD thesis, California Institute of Technology (Pasadena), 2014.

[11] S. W. C.Wynne, “Atmospheric dispersion correctors at the cassegrain focus,” Monthly

Notices of the Royal Astronomical Society, no. 220, pp. 657–670, 1986.

[12] refractiveindex.info.
[13] S. AG, “Refractive index and dispersion -technical information,” tech. rep., Schott AG, 2018.

AO bench design | May 30, 2018
[14] N. cameras, “Hnu128ao,” 2018.
[15] L. Jolissaint, Introduction a loptique pour les ingenieurs. HEIG VD, 2017.

AO bench design | May 30, 2018

## A OAPs focal lengths relations

This section describe the relation between the parental and the effective focal length for an off-axis parabola. The sketch figure 14 describes the situation with :

- EFL the effective focal length
- PFL the parental focal length
- (xS, yS) the coordinate of the ray intersection with the parabola
- the parabola of equation

y =

x

2
4PFL
− PFL | (22)


Figure 14: Sketch of a ray reflected on an OAP

The relation between EFL and PFL can be determined with the following set of equations.

xS | = EFL sin θ
yS | = EFL cos θ | (23)

AO bench design | May 30, 2018

Using (22) and (23) we have :

4PFL (yS + PFL) = x

2
S
4PFL (EFL cos θ + PFL) = (EFL sin θ)

2

4PFL² − 4PFL EFL cos θ − EFL² sin²
θ = 0

PFL1,2 =

4EFL cos θ ±

q
(−4EFL cos θ)

2 + 16EFL²
sin²
θ
2 ∗ 4
| =

1
2
EFL cos θ ±

q
EFL²

cos² θ + EFL²
sin²
θ

The final equation is :
2PFL = EFL (1 + cos θ) | (24)

AO bench design | May 30, 2018

## B Focal length of the relay lens between the pyramid

## and the CCD

Gauss :

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
| (25)

Thales :

CCD
L

=

|pi

| − |fLR|
|pi

CCD
L

= 1 −

fLR
pi

(26)

Mixing (25) and (26) :

CCD
L

=

fLR
po

(27)

In another hand :
F# = fOAP3

TT

=

po
L

(28)

Mixing (27) and (28) :
fLR = F# CCD | (29)

AO bench design | May 30, 2018

## C ADC design

### C.1 Scope

The previous report explains the different possibilities to configure an ADC. Here we are presenting the design we are going to implement for the case of the DAG telescope AO. This ADC will be for visible wavelength. The range is limited by the camera Nuvu spectral range and the star spectrum studied. We are taking only the Nuvu camera bandwidth into account for a first iteration.

### C.2 Amici principle

As said in the previous report, the Amici prisms are commonly used in the ADC systems. The ADCs are composed by a 2-doublet design which mixes two Amici prisms. This kind of prism is an alliance of two pieces of glass which have different dispersion (different refractive indexes). The materials must have the same refractive number for a mean wavelength so that at this frequency the incident and emergent rays are parallel (zero-deviation at λmean). The two prisms can be rotated around the optical axis in order to change the dispersion and compensate it for each wavelength. Shorter or longer wavelength than the middle one are deflected in opposite directions. When the angle between them is 180° the dispersion is reduced at its minimum.


Figure 15: 2-doublet Amici prisms design

Another design can be a three-glass Amici prisms, which is called triplet-design. It consists of the insertion of a anomalous dispersion glass between the two firstly introduced surfaces.

AO bench design | May 30, 2018


Figure 16: 2-triplet Amici prisms design [2]

The triplet-design seems to be appropriate for our case because it gives the best perfor-mance. According to Kopon thesis [2], the doublet corrects only the first order of chroma-tism while the triplet acts on both primary and secondary chromaticism aberration.

The system is made only by plane surfaces so that a plane front which go through the prisms should leave them as a plane front. In a collimated beam with a very narrow field of view the prisms combined thickness can be larger than the beam diameter [3].
We can also use vertex with a certain radius in a converging beam. This way we can change the F# leaving the ADC.
The doublet glass has to be designed in order to have a thermal expansion rate as close as possible between each glass to not break with the temperature changes. The internal reflection is also a parameter that we have to take into account because we want the ADC to transmit as much as possible light.

ADC design In order to design our ADC, we need to collect some information about its position in the AO bench,the dispersion of the atmosphere for our parameters, the field of view (FoV) and wavelength bandwidth it has to work in.

C.3 | Model of the atmosphere refraction
C.3.1 | Atmosphere refraction index

First, we need to model to atsmophere dispersion (refractive index) depending on the wavelength. The simulation of the atmosphere refractive index is based on Ciddor’s ap-

AO bench design | May 30, 2018

proach [4] which is a compilation of all previous equations for the visible and near infrared. The following set of equations are used to model the atmosphere refraction :

10⁸
(nas − 1) = k1/
k0 − σ

2

+ k3/
k2 − σ

2

(30)

(nasx − 1) = (nas − 1) h

1 + 0.534 × 10⁻⁶
(xc − 450)i
(31)

10⁸
(nws − 1) = 1.022 ×
ω0 + ω1σ

2 + ω2σ

4 + ω3σ

6

(32)
nf inal | = (ρa/ρaxs) (naxs − 1) + (ρω/ρωs) (nωs − 1) | (33)

where the parameters are defined as follow :

- the wave number
σ = 2π/λ [µm

−1
]
- Constants involved in the standard phase and group refractivities of dry air [4]
k0 = 238.0182, k1 = 5792105, k2 = 57.362, k3 = 167917 [µm⁻²
]
- nas the refractive index of standard air at T=20°C, 101325 Pa, 0 % humidity, 450 ppm of CO2
- for now, I took the concentration of CO2 in the air of xc = 450 ppm (standard) so equation (31) becomes nasx = nas but we can change that easily changing the xc parameter in the code
- nasx the refractive index of xc ppm of CO2 at T=20°C, 101325 Pa, 0 % humidity
- Constants involved in the standard phase and group refractivities of water vapor [4] ω0 = 295.235 [µm⁻²

], ω1 = 2.6422 [µm⁻²

], ω2 = −0.032380 [µm⁻⁴

], ω3 = 0.004028 [µm⁻⁶
]
- nωs the refractive index of water vapour at T=20°C, 1333 Pa
- ρa [kg/m³
] the humid air density calculated equation (34)
- ρaxs [kg/m³
] the density of dry air at standard conditions calculated equation (35)
- ρω [kg/m³
] the density of water vapour calculated equation (36)
- ρωs [kg/m³
] the density of water vapour at standard conditions calculated equation (37)

AO bench design | May 30, 2018

Calcul of the humid air density

ρa =

P Ma
Z R T
1 − xV
1 −

MV
Ma
| (34)

P = P0

1 −

∆T H
T

!

Ma = (28.9635 + 12.011(xCO2 − 0.0004)) × 10⁻³

Z = 1 −

| P T
h
| a0 + a1 t + a2 T 2 + (b0 + b1 t) ∗ xv + (c0 + c1 t) ∗ x

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
d + e ∗ xv²

with :

- P0 = 1.01325 × 10⁵
| [Pa] the normal pressure at altitude 0 m;
- ∆T = 0.0065 [K] the vertical gradient of temperature (0.65K for 100 m) [5]
- T0 = −10 [°C] mean temperature from DAG-AWOS1
- H = 3170[m] Karakaya altitude
- Ma [kg/mol] the density of dry air with xCO2 = 0.0004 [6]
- MV = 18.01528 × 10⁻³
| [kg/mol] the mole mass of water
- R = 8.314510 [J/mol/K] the molar gas constant
- Z the compressibility with t the temperature in [°C] and the following constants and
| parameters [6] :

– a0 = 1.58123 × 10⁻⁶

[K*Pa⁻¹

], a1 = −2.9331 × 10⁻⁸
[Pa

−1
], a2 = 1.1043 ×
10⁻¹⁰ [(K*Pa)⁻¹

], b0 = 5.707 × 10⁻⁶

[K*Pa⁻¹

], b1 = −2.051 × 10⁻⁸

[Pa⁻¹
], c0 =
1.9898×10⁻⁴

[K*Pa⁻¹

] c1 = −2.376×10⁻⁶

[Pa⁻¹

], d = 1.83×10⁻¹¹ [K²Pa⁻²
], e =
−0.765 × 10⁻⁸

[K²Pa⁻²
]
– xv =RH f

Psv
P mole fraction of water vapour, RH the relative humidity (taken here as 0.8)
– f = α + βP + γT²
| increasing factor (α = 1.00062 [-], β = 3.14 × 10⁻⁸
| [Pa],
γ = 5.6 × 10⁻⁷
| [K⁻²
| ])
– P sv = exp | AT² + BT + C + D
| T
| the saturation vapour pressure of moist air
(A = 1.2378847 × 10⁻⁵
| [K⁻² ], B = −1.9121316 × 10⁻² [K⁻¹
| ], C = 33.93711047
[-], D = −6.4341645 × 10³
| [K])

AO bench design | May 30, 2018

Calcul of density of dry air at standard conditions

ρaxs =

P0

RgasT0

(35)

with Rgas = 287.05 [J/kg/K] [7].

Calcul of the water vapour density

ρω =

PwMV
R T

(36)

With :

- MV = 18.01528 × 10⁻³
[kg/mol] the mole mass of water
- Pw [mb] partial pressure of water vapour (mmHg2Pa = 133.322365 and P sat [mmHg] valid between -50°C and 200°C)

P sat = exp
46.784 −

6435
T

− 3.868 log(T)

Pw = P sat ∗ RH ∗ mmHg2Pa

Calcul of the water vapour density at standard conditions

ρωs =

Pw0MV
R T0

(37)

With :

- MV = 18.01528 × 10⁻³
[kg/mol] the mole mass of water
- Pw0 [mb] partial pressure of water vapour (mmHg2Pa = 133.322365 and P sat0 [mmHg] valid between -50°C and 200°C)

P sat0 = exp (46.784 − 6435/(T0) − 3.868 log(T0))

Pw0 = P sat0 ∗ RH ∗ mmHg2Pa

AO bench design | May 30, 2018
C.3.2 | Atmosphere refraction equation

The refraction of the atmosphere is computed with the equation [8]:

R(λ, z) = κ (n(λ) − 1) (1 − β) tan(z) − κ (n(λ) − 1)

β −

(n(λ) − 1)
2

!
tan³
(z) (38)

with

- β = 0.001254
| T(K)

273.15
the effective height of the observatory above the surface of the earth [8]
- κ = 1 for a spherical Earth surface [8] or instrumental correction no more useful [9]

This equation (38) is valid only for zenith angle ¡ 75°. We can even neglect the second term for zenith angles ¡ 65° [10]. The limit of zenith angle of our computation is set to 70°so the entire equation is set.

C.3.3 Glasses for the ADC

The choice of glass depends on the range of zenith angles, the wavelength interval, the maximum size of the blanks and the cost [11]). Most of the glass couple in the Amici conception are flint/crown pairs plus an anomalous dispersion glass inserted for the triplet design.
The glass choice is made in a data base built from Schott and Ohara catalogues. The data are taken from [12] where we can download glasses properties from many different suppliers. The data are sorted to extract Sellmeier coefficients [13] in order to compute the refractive index of each glass depending on the wavelength with the equation (39).

n

2

(λ) = 1 + B1λ

2
λ

2 − C1

+

B2λ

2
λ

2 − C2

+

B3λ

2
λ

2 − C3

(39)

with Bi and Ci Sellmeier coefficients for λ in µm [13].

The final glass data base with the refractive index reported is generated for three wave-lengths : le smallest, the highest and the mean wavelength. These are for our case the Nuvu camera [14] bandwidth limits λmin = 0.3 [µm] and λmax = 1.0 [µm] and the maximum quantum efficiency corresponding wavelength λmean = 0.6 [µm].

AO bench design | May 30, 2018
C.3.4 | Beam propagation through the ADC

In order to compute de dispersion through the ADC a geometrical and refraction set of equations have been implemented. The sequence of these equations is listed bellow. I will follow the light on the figure 17 to describe each step.


Figure 17: Sketch of the refraction through the ADC

The refractive index of the I-th glass is nI (λi). To simplify the notation, we just write nI . We apply the sign convention described in the course material [15].

At the entrance we have the vector

xE
zE = 0
n0 sin αE

At the entrance 0E, we have a refraction

xE
zE = 0
nA sin α1

which gives :

α1 = arcsin
n0
nA

sin αE

AO bench design | May 30, 2018

At the first interface AB, we arrive with the coordinates

xA
zA
nA sin (α2)


Figure 18: Decomposition of the parameters at an interface

We can determine this vector using the following equations from figure 18 :

X =

dA
tan θA

;

X−xA
X =

zA
dA

; zA =

xE−xA
tan α1

Then we find :

xA =

xE−dA tan α1
1−tan α1 tan θA
zA =

xE−xA
tan α1
α2 = α1 + θA

At the interface AB, we have a refraction

xA
zA
nB sin α3

which gives :

α3 = arcsin
nA
nB

sin α2

AO bench design | May 30, 2018

At the interface BC, we arrive with the coordinates

xB
zB
nB sin (α4)

We can determine this vector using the following equations from figure 18 :

X =

xA
tan αA

;

xB
X−Q−dB+m = tan αA ; m = dA + dB − zB ; m = xB tan θB ; Q = dA − zA ;

αA = α3 + θA

Then we find :

xB | = xA−tan αA(dA+dB−zA) 1−tan αA tan θB
zB | = dA + dB − xB tan θB
α4 | = αA + θB

At the interface BC, we have a refraction

xB
zB
nC sin α5

which gives :

α5 = arcsin
nB
nC

sin α4

At the interface C0, we arrive with the coordinates

xC
zC
nC sin (α6)

We can determine this vector using the following equations from figure 18 :

X =

xB
tan αB

;

xC
X−Q−dC +m = tan αB ; m = dA + dB − zB ; m = xC tan θC ; Q = dA + dB − zB ; αB = α5 + θB

Then we find :

xC | = xB−tan αB(dA+dB+dC −zB) 1−tan αB tan θC
zB | = dA + dB + dC − xC tan θC
α6 | = αB + θC

AO bench design | May 30, 2018

At the interface C0, we have a refraction

xC
zC
n0 sin α7

which gives :

α7 = arcsin
nC
n0

sin α6

The output angle with respect to the optical axis αS = α7 − θC This αS is the dispersion angle of the prism : Rprism = αS.

C.3.5 The metric definition

Now we have computed the dispersion of the atmosphere and the ADC. We want the smallest total dispersion so we investigate all ADC configurations in order to minimize it. The metric we use comes from [10] to calculate the efficiency of our prism combination :

Eff (prism parameters) = X

λi

(Rprism (λi

; prism parameters) − Ratm (λi))² (40)

C.3.6 Internal reflection

In parallel of the dispersion computation, we calculate the total internal reflection of the ADC. If the refractive index of two joint glasses are too different then we will loose a lot of intensity reflected on the interface. The external faces of the ADC will be coated. The determination of the total internal reflectivity is developed below.
The parameters are :
- αZ = [αE; α1; αA; αB; αS] [rad] array of the rays angle wrt the optical axis
- αI = [α1; α2; α3; α4; α5; α6; α7] [rad] array of the rays angles wrt the normal the vertex (refraction angle)
- n = [n0; nA; nB; nC; n0] medium refractive index
- d = [zA, zB − zA, zC − zB] [mm] distances on the optical axis between each medium change on the ray path

AO bench design | May 30, 2018

At the 1rst interface AB, we have :

r[1] = n[3] cos αI [2] − n[2] cos αI [3]
n[3] cos αI [2] + n[2] cos αI [3] | (41)

Taking the recursive initialization term U(1) = r(1) we have for p = 2:

r[p] = n[p + 1] cos (αI [p]) − n[p] cos (αI [p + 1])
n[p + 1] cos (αI [p]) + n[p] cos (αI [p + 1]) | (42)

U[p] =

U[p − 1] + r[p] exp
2π
λ

cos (αZ[p]) d[p − 1]

1 + U[p − 1] r[p] exp
2π
λ
cos (αZ[p]) d[p − 1] | (43)

Using equation (43) we can calculate the reflection coefficient for (p+ 1) number of glasses. In our case we have only 3 glasses so the total reflection (without taking external faces into account) is U[2].

### C.4 ADC design optimization

The efficiency of a combination (glass, angle, thickness) is computed by the function Re-

fraction calculs geometriques 20180302.m. The fmincon Matlab algorithm is used to find minimum of this constrained nonlinear multivariable function. The parameters are the geometrical coefficients for one set of glass. When the optimum is found for a combination of glass, the efficiency and internal reflection are given as outputs.

The global matrix is made from two for-loops that look for all glasses from the catalogues Schott and Ohara. We decide to have the same glass type for the external wedges in order to simplify the anti-reflection coating process. This would give us the possibility to coat the prism at once and so reduce the cost. The refractive index of the middle wedge glass is chosen larger than the middle one to save effort and cost on the coating. In the optimization process on Matlab, when this refractive index (for λmean is larger than external one the loop stops. The outputs are set to 20’000 (arbitrarily large to oust them).
The wavelength for which the refraction is calculated are taken from the Nuvu camera quantum efficiency curve : λmin = 300 nm, λmean = 600 nm and λmax = 1000 nm. The zenith angle is set to 70°.

AO bench design | May 30, 2018

## D DimensionnementOAPs.py

1 # −∗− c odin g : u t f −8 −∗−
”””
3 Created on F ri May 18 1 0: 2 7: 4 3 2018
This code compute the f o c a l l e n g t h o f the OAPs and the image p o s i t i o n . 5 @author : audrey . bouxin
”””
7 import numpy a s np
import m a t pl o tli b . p y pl o t a s p l t

9
” Parameters ”
11 | DEG2RAD = np . pi / 1 8 0;
theta OAP0 | = 20∗DEG2RAD; #[ rad ] | pour l ’OAP0
13 | theta OAP1 = theta OAP0 ;
theta OAP2 | = 20∗DEG2RAD; #[ rad ] | pour l ’OAP2
15 | #theta OAP3 | = 10∗DEG2RAD; | #[rad ] | pour l ’OAP3
ExP2FP = 1 0 3 3 8. 7 4; | #[mm]
17 | dExP | = 7 2 7. 4 0 4 6; | #[mm]
DDM | = 3 2 . 7 ; | #[mm]

19
| # f o r OAP0
21 | alph a = np . a r c t a n (dExP∗0. 5 /ExP2FP) ; | #[ rad ]
PFL OAP0 =(DDM) /2/(−1/np . tan ( theta OAP1+alph a ) +(1/(np . tan ( theta OAP1+alph a ) ) ∗∗2+1) ∗∗0.5+1/ np . tan ( theta OAP1−alph a ) −(1/(np . tan ( theta OAP1−alph a ) )
∗∗2+1) ∗ ∗ 0. 5 ) ; | #[mm] pour l ’OAP0
23 | EFL OAP0 = 2∗PFL OAP0/(1+np . c o s ( theta OAP1 ) ) ;
p r i n t ( ’PFL OAP0 ( e s tim ) : ’ , PFL OAP0)

25

27 PFL OAP0 = 4 4 5 . 0 ;
p r i n t ( ’PFL OAP0 : ’ , PFL OAP0)
29 EFL OAP0 = 2∗PFL OAP0/(1+np . c o s ( theta OAP1 ) ) p r i n t ( ’EFL OAP0 : ’ , EFL OAP0)
31 po = −(PFL OAP0+ExP2FP) ;
pi = po∗PFL OAP0/ ( po+PFL OAP0) ;
33 | p r i n t ( ’ pi (DM) | : ’ , pi )

AO bench design | May 30, 2018
35 | # # pour l ’OAP1
fOAP1 = PFL OAP0

37
# pour l ’OAP2

39 p r i n t ( ’−−−−−−−−−−−−−−−−−−−−−−−−−OAP2 : ’ ) TTangle = 10∗DEG2RAD;
41 | DTT = 10#∗np . c o s ( TTangle ) ; | #[mm]
fOAP2 = DTT/DDM∗fOAP1 ; | #[ −]
43 | alph a = np . a r c t a n (DTT∗0. 5 / fOAP2 ) ; | #[ rad ]
PFL OAP2 = (DTT/ 2 ) /2/(−1/np . tan ( theta OAP2+alph a ) +(1/(np . tan ( theta OAP2+ alph a ) ) ∗∗2+1) ∗∗0.5+1/ np . tan ( theta OAP2 ) −(1/(np . tan ( theta OAP2 ) ) ∗∗2+1)
∗ ∗ 0. 5 ) | #[mm] pour l ’OAP2
45 | EFL OAP2 = 2∗PFL OAP2/(1+np . c o s ( theta OAP2 ) )
p r i n t ( ’PFL OAP2 : ’ , PFL OAP2)

47 #
# # Pour l ’OAP3

49 | # p y r r o o f = 2 0; | #[um]
# lambda | = 0 . 6 ; #[um]

51 | # fnum = 60;#2∗ p y r r o o f /lambda ;
# alph a = atan ( 1 / (fnum ∗2 ) ) ; | #[rad ] pour l ’OAP3

53 | # DTT = 2 5 . 1 1 ;
# PFL OAP3 = (DTT/ 2 ) /2/(−1/ tan (theta OAP3+alph a ) +(1/(tan (theta OAP3+alph a ) ) ∗∗2+1) ∗∗0.5+1/ tan (theta OAP3 ) −(1/(tan (theta OAP3 ) ) ∗∗2+1) ∗ ∗ 0. 5 ) #[mm] pour l ’OAP3

55 # EFL OAP3 = 2∗PFL OAP3/(1+ c o s (theta OAP3 ) )

../DimensionnementOAPs.py

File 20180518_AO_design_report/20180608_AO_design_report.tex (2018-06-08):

\documentclass[12pt,a4paper]{article}

\input{def/options}

\begin{document}
\input{def/pagetitle}
\setlength{\parindent}{0pt}%20pt}

%\tableofcontents

\section*{Acronyms}
\afterpage{\cfoot{\thepage}}

\begin{minipage}[c]{0.5\textwidth}
\begin{center}
\begin{tabular}{p{13mm}|p{55mm}}
aO & active Optics \\
AO & Adaptive Optics \\
CCD & Charge Coupled Device\\
CMOS & Complementary Metal Oxide Semiconductor\\
DAG & Dogu Anadolu Gozlemevi (East Anatolian Observatory)\\
DM & Deformable Mirror\\
FCL & Field Correction Lens\\
FoV & Field-of-View\\
FWHM & Full Width at Half Maximum\\
NCPA & Non Common Path Aberrations
\end{tabular}
\end{center}
\end{minipage}
\begin{minipage}[c]{0.5\textwidth}
\begin{center}
\begin{tabular}{p{16mm}|p{55mm}}
NGS & Natural Guide Star \\
OTF & Optical Transfer Function\\
P2V & Peak-to-Valley\\
PSF & Point Spread Function\\
PSF-R & PSF Reconstruction\\
PWFS & Pyramid WFS\\
RMS & Root Mean Square\\
SH-WFS & Shack-Hartmann WFS\\
SNR & Signal-to-Noise Ratio\\
TT & Tip-Tilt\\
WFS & Wavefront Sensor\\
WFE & Wavefront Error
\end{tabular}
\end{center}
\end{minipage}
\newpage

\section{Scope of this document}

This document presents the DAG adaptive optics (AO) optical train design and optimization.

\section{Introduction}
There are several mandatory points we have to handle :
\begin{itemize}
	\item the exit pupil has to be imaged on the DM (Deformable Mirror);
	\item the DM diameter is fixed to the DM-468 clear aperture from ALPAO; that means \O $33$ mm;
	\item the exit pupil of the telescope has to be imaged on the TT (Tip-Tilt) mirror for the P-WFS modulation;
	\item the beam has to converge on the pyramid apex;
	\item the angle of the beam that arrives onto the pyramid apex is calculated in order to get a diffraction limited PSF size of 2 times the pyramid roof;
	\item the exit pupil has to be imaged onto the Nuvu EMCCD detector;
	\item the beam footprint diameter onto the detector has to be defined accordingly to the oversampling criterion (explained section~\ref{subsec:Pup2CCD}).\\
\end{itemize}

We use off axis parabolas (OAPs) for all our design to reduce the aberrations (compared to lenses).
We have added one more constraint on the design which is to have parallel beam arriving or leaving each off axis parabola in order to limit the spherical aberrations.\\

The fixed parameters are resumed here :
\begin{itemize}
	\item exit pupil diameter : \diameter$_{\text{ExtP}} = 727.4046$ mm;
	\item distance from the exit pupil to the focal plane : $\overline{\text{ExP-FP}} = 10338.74$ mm; 
	\item DM diameter : \diameter$_{\text{DM}} = 33.0$ mm;
	\item pixel size of the Nuvuu EMCCD AO : $\text{PxSize} = 24$ $\mu$m
\end{itemize}
\newpage
In order to design the AO bench we started with the telescope model. Indeed, we would try to compensate for the field of curvature introduced by the mirrors of the telescope with the off-axis parabolas (OAP) of the AO. The Zemax model of the telescope shows a curvature radius of about 1255 mm.
\begin{figure}[H]
	\begin{center}
		
		\caption{Zemax model of the telescope}\label{fig:Zemax_model_telescope}
	\end{center}
\end{figure}

Concerning off-axis aberrations for a future GLAO mode, they are totally dominated by the atmospheric aberrations through this telescope (30~nm for 2' FoV), so we do not need a field correction lens. In a first approach, we thought we should have one nearby the focal plane but this is not the case anymore.

\newpage
\section{Design development and optimization}
A preliminary design have been set for the PDR and the main points are summarized at each optimization step of this report.

\subsection{Imaging the exit pupil of the telescope onto the DM}
The first section consists on an imaging system of the telescope exit pupil onto the DM. The beam has to be collimated and the footprint has to take the entire clear aperture of the DM (for the DM-468 from ALPAO $\diameter_{\text{DM}}$~=~33~mm).\\
The beam on the DM has to be reflected with a certain angle otherwise the reflected beam comes back on itself. The maximum acceptable angle can be calculated considering the position error of the beam per actuator on the DM. We can align the beam with a registration error due to this elliptical beam footprint of $1/10^{th} \Lambda$ ($\Lambda$ the actuator pitch $= 1.5$ mm for the ALPAO DM-468). In order for the projected beam diameter to be no more than 10\% smaller than the DM diameter on both side, the tilt of the DM must be no more than $\alpha$~(figure \ref{fig:OAP0_DM_diam_beam_diam})~:

\noindent\begin{minipage}{.45\textwidth}
\begin{eqnarray}
	\alpha &= &\arccos\left(1-\frac{1}{5}\frac{\Lambda}{\diameter_{\text{DM}}}\right)\nonumber\\
	\alpha &= &\arccos\left(1-\frac{1}{5}\frac{1.5}{33}\right)\nonumber\\
	\alpha &= &7.73^{ \circ}\label{eq:alphaDM}\\
	2\alpha &= &15.46^{ \circ}\nonumber
\end{eqnarray}
\end{minipage}
\begin{minipage}{.45\textwidth}
   \centering
   \begin{figure}[H]
	\begin{center}
		
		\caption{Sketch of the input and output beam depending on the tilt angle of the DM}\label{fig:OAP0_DM_diam_beam_diam}
	\end{center}
\end{figure}
\end{minipage}

The input beam diameter is then :
\begin{equation}
	\diameter_{\text{DM-beam}} = \diameter_{\text{DM}} \cos{\alpha} = 33\times \cos{(7.73)} = 32.7 \text{ mm}
\end{equation}

In order to have a collimated beam on the DM with a diameter of $\diameter_{\text{DM-beam}}$, the focal length of the OAP0 is calculated by the following sequence of equations. To visualize the parameters needed and the context we can look at figure~\ref{fig:sketch_ray_tracing_OAP0}. The OAP is tilted with an angle $\theta$ and its corresponding reference coordinates is $\left(0,x',y'\right)$. The ray $\Delta$CR corresponds to the chief ray, $\Delta\alpha u$ is the "upper" marginal ray and $\Delta\alpha b$ is the "bottom" marginal ray. The origin is placed at the focal plane of the telescope.

\begin{figure}[H]
	\begin{center}
		
		\caption{Ray tracing of a tilted parabola}\label{fig:sketch_ray_tracing_OAP0}
	\end{center}
\end{figure}
In the reference coordinates $\left(0,x',y'\right)$, we have (with PFL the Parental Focal Length of the OAP):
\begin{itemize}
	\item equation of the parabola $\theta$ : 
	\begin{equation}
	y' = \frac{x'^2}{4\,\text{PFL}}-\text{PFL}	\label{eq:parabola_theta}
	\end{equation}
	\item equation of $\Delta\alpha u$ : \begin{equation}
	y' = -\frac{1}{\tan\left(\theta+\alpha\right)}x' \label{eq:delta_alphau}
	\end{equation}
	\item equation of $\Delta\alpha b$ : \begin{equation}
	y' = -\frac{1}{\tan\left(\theta-\alpha\right)}x' \label{eq:delta_alphab}
	\end{equation}
\end{itemize}
%
%Determination of $x'_{\text{CR}\theta}$ (intersection between parabola $\theta$ and $\Delta$CR) :\\ \eqref{eq:parabola_theta} = \eqref{eq:delta_CR}\\
%\begin{equation}
%	x'_{\text{CR}\theta} = 2\,\text{PFL}\left(-\frac{1}{\tan\theta}+\sqrt{\frac{1}{\tan^2\theta}+1}\right)
%\end{equation}

Determination of $x'_{\text{Ex}\theta\,\,u}$ (intersection between parabola $\theta$ and $\Delta\alpha u$) :\\ \eqref{eq:parabola_theta} = \eqref{eq:delta_alphau}\\
\begin{equation}
	x'_{\text{Ex}\theta\,\,u} = 2\,\text{PFL}\left(-\frac{1}{\tan\left(\theta+\alpha\right)}+\sqrt{\frac{1}{\tan^2\left(\theta+\alpha\right)}+1}\right)
\end{equation}

Determination of $x'_{\text{Ex}\theta\,\,b}$ (intersection between parabola $\theta$ and $\Delta\alpha b$) :\\ \eqref{eq:parabola_theta} = \eqref{eq:delta_alphab}\\
\begin{equation}
	x'_{\text{Ex}\theta\,\,b} = 2\,\text{PFL}\left(-\frac{1}{\tan\left(\theta-\alpha\right)}+\sqrt{\frac{1}{\tan^2\left(\theta-\alpha\right)}+1}\right)
\end{equation}

In order to have the OAP0 output beam diameter equal to the DM clear aperture we have~:
\begin{equation}
	x'_{\text{Ex}\theta\,\,u}-x'_{\text{Ex}\theta\,\,b} = \diameter_\text{DM-beam}
\end{equation}
The parental focal length (see appendix~\ref{sec:EFL2PFL}) of OAP0 is :
\begin{equation}
	\text{PFL} = \frac{1}{2}\frac{\diameter_\text{DM-beam}}{-\frac{1}{\tan\left(\theta+\alpha\right)}+\sqrt{\frac{1}{\tan^2\left(\theta+\alpha\right)}+1}+\frac{1}{\tan\left(\theta-\alpha\right)}-\sqrt{\frac{1}{\tan^2\left(\theta-\alpha\right)}+1}}
\end{equation}
Using the equation~\eqref{eq:EFL2PFL} described in appendix~\ref{sec:EFL2PFL} we can transform the parental focal length into the effective focal length.\\

For the OAP0 the angle $\alpha_{\text{OAP0}}$ is
\begin{eqnarray}\label{eq:alpha_OAP0}
	\alpha_{\text{OAP0}} &= &\arctan\left(\frac{\diameter_{\text{ExP}/2}}{\overline{\text{ExP-FP}}}\right)
\end{eqnarray} 
The numerical application of \eqref{eq:alpha_OAP0} with $\diameter_{\text{ExP}} = 727.4046$ mm and $\overline{\text{ExP-FP}} = 10338.74$ mm gives $\alpha_{\text{OAP0}}  = 2.015\degree$, the aperture demi~angle of the beam arriving on the first OAP.\\

After the discussion we had with Paolo Spano, we took his advice into account and choose the parabola tilt angle according to the following precept : $\theta= 35\degree$ is a critical choice and $\theta > 35\degree$ is a nightmare (manufacturing and alignment). We should take an tilt angle smaller than 30$\degree$ to be realistic and the smaller the best.\\

We set the parabola tilt angle to $\theta = 10\degree$ in order to keep this angle very small. This way we can see that the DM is quite close to the telescope focal plane (about 2~cm). We choose to increase this distance with a view to update the entire design to a GLAO one (and a larger FoV). We finally set the tilt angle of the OAP0 to $\theta = 15\degree$ to keep it as small as possible to limit aberrations.\\

Using these inputs the focal length of the OAP0 is (appendix~\ref{app:DimensionnementOAPs}): $\text{PFL}_{\text{OAP0}} = 456.99\,\text{mm}	\nonumber$.\\
This value is too specific so we round it to\footnote{In Zemax, we enter the $\text{PFL}_{\text{OAP0}}$ and not the effective focal length in the coordinate break surface because using it, the translation is done before the tilt angle. This is why if we enter the translation in a surface before the coordinate break we cannot use the same length (we would then write the $\text{EFL}_{\text{OAP0}}$)}~:
\begin{equation}
	\text{PFL}_{\text{OAP0}} = 455\,\text{mm}	\nonumber
\end{equation}

The image of the exit pupil given by OAP0 gives the position of the DM. Its position $p_i$ relative to the OAP0 vertex is given by (we use Gauss law)~:
\begin{eqnarray}
	p_i &= &\frac{p_o\,\text{PFL}_{\text{OAP0}}}{p_o+\text{PFL}_{\text{OAP0}}}\\
	p_i &= &\frac{-(10338.74+455)455}{-10338.74}\\
	p_i &= &477\,\text{mm}
\end{eqnarray}
The Zemax "pick up pupil position" macro is used to get the perfect DM position wrt the OAP0. The DM is then at $p_i = 491.50$~mm. Even if we understand that we cannot align the DM reflecting surface with this accuracy, we keep it in the Zemax model and we will work on that during the tolerancing analysis\footnote{We always keep all the digits during an AO design in order to see what are the best results we can obtain with an ideal system.}. \\

\begin{wrapfigure}[6]{r}{60mm}
  \vspace{-1cm}
  \centering
  
  \caption{Tilted image of the pupil}\label{fig:DM_pupil_tilt}
\end{wrapfigure}
The image of the pupil through a tilted OAP is also tilted~(see~\cite{cite:Design90degOAP}). This creates pupil aberrations. Here we want to place the DM at this pupil position. When we work with OAPs the image stop after an OAP is not perpendicular to the optical axis.\\

The OAP introduce a tilt angle of the image plane. If we tilt the DM in the opposite position of this OAP-introduced tilt angle we add pupil aberrations whereas if we tilt it the same direction we can compensate for it. 

%The image of the pupil through a tilted OAP is also tilted~(see~\cite{cite:Design90degOAP}). This creates pupil aberrations.
%\begin{figure}[H]
%	\begin{center}
%		\includegraphics[width=.6\linewidth]{images/DM_pupil_tilt.PNG}
%		\caption{Tilted image of the pupil}\label{fig:DM_pupil_tilt}
%	\end{center}
%\end{figure}
%Here we want to place the DM at this pupil position. When we work with OAPs the image stop after an OAP is not perpendicular to the optical axis. The OAP introduce a tilt angle of the image plane. If we tilt the DM in the opposite position of this OAP-introduced tilt angle we add pupil aberrations whereas if we tilt it the same direction we can compensate for it. 

\begin{figure}[H]
%\centering
\begin{subfigure}[b]{0.45\textwidth}
	\begin{center}
		
		\caption{Layout}\label{fig:FP_OAP0}
	\end{center}
\end{subfigure}
\begin{subfigure}[b]{0.45\textwidth}
\begin{center}
		
		\caption{Zemax footprint diagram of the beam on the DM}\label{fig:DM_beam_footprint}
	\end{center}
\end{subfigure}
\caption{Zemax model of the 1rst part of the AO design}
\end{figure}

The beam footprint on the DM shows that all the field fits inside the clear aperture. The maximum diameter is equal to 32.9656 mm ($< 33$ mm \hl{To Paolo : is this okay ? because we are close to the limit... should I take a focal length of 450~mm which gives us a footprint diameter on the DM of 32.603~mm ? maybe it is okay for modelling an ideal case but I should review this value for our real case during the tolerancing analysis..}). The angle of the DM is set to~-7.73\degree~(equation~\eqref{eq:alphaDM}),and not 7.73\degree as explained above (pupil aberration compensation).

\subsection{Imaging the pupil on the TT modulation mirror and focus on the pyramid apex}

\subsubsection{Create an image of the pupil}
We need to image the pupil on the TT modulation mirror. Moreover, we know that to compensate for the aberration introduced by OAP0 we can use an OAP1 with the same focal length. The F/D ratio would stay the same as the telescope one which is favourable for the science path.\\
Figure~\ref{fig:Zemax_model_FP_OAP1} shows that to model this combination we use the "chief ray" solve on Zemax (Lens data) to keep the coordinates following the beam path (using the on-axis ray). OAP1 is placed at the exact inverse position of OAP0 in order to compensate for its aberrations so the intermediate focal plane is near the telescope focal plane.\\

\begin{figure}[H]
	\begin{center}
		
		\caption{Zemax model from the telescope beam to the intermediate focal plane}\label{fig:Zemax_model_FP_OAP1}
	\end{center}
\end{figure}
We use an optimization (smallest spot radius) to go to the best focal plane (surface \#23 thickness is set as variable) and in order to consider the field curvature we set the radius of the image plane variable. The optimization using a merit function (Type~:~P2V, Criteria~:~Spot~Radius, Reference~:~Chief~Ray) is done on the image surface to get the smallest spot radius of the central beam (FoV = 0'). We can see that the spot diameter varies between 0.345~$\mu$m and 0.009~$\mu$m (the center of the FoV) but when we look the spots with the Airy disk we can say that the beam is well focused.\\
However, the radius of the image curvature is smaller than the telescope output field of curvature so we did not compensate for that, instead we increase it (we will see how we could work on that or not \hl{Paolo : how could I compensate for it ?}).\\

\subsubsection{Bend the beam}
In order to avoid to send back the beam on the focal plane and because we would like to place the dichroic nearby the intermediate focal plane, we fold the beam after the DM with a flat mirror.
\begin{figure}[H]
	\begin{center}
		
		\caption{Zemax model from the telescope beam to the intermediate focal plane with a fold mirror after the DM}\label{fig:FP_2_intFP_FoldMirror}
	\end{center}
\end{figure}
Figure~\ref{fig:FP_2_intFP_FoldMirror} shows the new design with a folding mirror tilted at 20\degree. For more clarity we apply the real aperture size of the OAPs on layout 2. We can see on the footprint diagram that we can use two OAPs of 30~mm of diameter. Actually, manufacturers can guaranty the surface quality on 90\% of the diameter so the useful optical surface diameter is 27~mm (according to the discussion with Mirsad). The maximum diameter of the beam footprint (for a FoV~=~1') is about 50.25~mm. However, we should be careful and verify during the tolerance analysis that when we move the OAP in the alignment precision range we can do, the entire beam stays reflected on the OAP (no vignetting). Concerning the folding mirror, we can use a diameter of 2~inches (footprint diameter~=~45.72~mm) it is positioned at 286~mm from the DM (same as above, we have to check during the tolerancing that we do not have vignetting when moving around this position).\\

After redoing the optimization of the intermediate focal plane position and the image radius of curvature we found spot diameters vary from 0.009~$\mu$m (on-axis) to 0.436~$\mu$m (0.5') across the FoV (see figure~\ref{fig:IntermediateFP_SpotDiagram}).\\
\begin{figure}[H]
	\begin{center}
		
		\caption{Spot diagram at the intermediate focal plane for the AO FoV and the WFS path FoV}\label{fig:IntermediateFP_SpotDiagram}
	\end{center}
\end{figure}

\subsubsection{Sending the light to science instruments}
We want to introduce a dichroic membrane nearby the intermediate focal plane to reduce its diameter. Then a folding mirror is added to send the light to the instruments. This allows avoiding a large incidence angle on the dichroic which would generate a large reflection loss due to polarisation. The dichroic tilt angle is set to 20\degree and in order to send the beam collinear to the output of the telescope, the folding mirror is put at 7\degree of tilt.
\begin{figure}[H]
	\begin{center}
		
		\caption{Zemax model from the telescope focal plane to the intermediate science light}\label{fig:Zemax_model_FP_Dichroic}
	\end{center}
\end{figure}
The dichroic membrane send the infrared light to the science and let the rest going through the WFS sensor path. The cutting line should be around 900~nm (according to the Nuvu camera QE). The FoV at the WFS path is about 8'' which corresponds (for Zemax) to a demi-FoV of 8/(2*3600)~=~0.001111\degree.\\

We could also replace the folding mirror with an OAP in order to make the beam collimated again to avoid having very large diameter beam arriving at the instrument entrance.
\hl{analyse this possibility !!!!!!!!!!!!!!!!!!!!!!!!!!!!!!!!!!!!!!!!!!!!!!!!!}

\subsubsection{Imaging the pupil on the TT modulation mirror and focus on the pyramid apex}\label{subsubsec:TTMM}
Now, as the OAP0 and OAP1 are the same, this optical configuration creates an image of the pupil of the same diameter at the same distance from the FP as the exit pupil.\\ 
It is so not possible to use it to place the TT modulation mirror which has to be 10~mm in diameter and at a reasonable distance from FP.
\hl{FOR these reasons........................................ we take a TT modulation mirror of \diameter 0.5~inch mounted on the fast tip-tilt platform S-331 from PI.}\\

We know that we need to arrive on the pyramid roof (P-WFS) with~:
\begin{eqnarray}
	\text{PSF FWHM} &> 2\text{pyramid roof}\nonumber\\
	\lambda\frac{f}{D} &> 2\text{pyramid roof}\nonumber\\
	\frac{f}{D}&>2\frac{\text{pyramid roof}}{\lambda}\label{eq:FnumEq}
\end{eqnarray}

Taking a pyramid roof of about $20~\mu$m according to Jean-Pierre Veran (private communication) at $\lambda~=~0.6~\mu$m we have~:~~$F\# = 66.7\label{eq:Fnum}$

We round this value to F\#~=~60 (we need to investigate the minimum pyramid roof size that can be manufactured).\\

We want then a power that takes the beam with a F\# of 14 and brings it to 60. The TT modulation mirror is placed in this converging beam at the pupil position. We choose to take an imaging doublet lens because the wavelength range in the WFS path is 500~nm to 900~nm and achromatism can be easily compensated.\\
At first approximation, we can do a geometrical dimensioning. We use a drawing software and apply the constraints to calculate which focal length and distance from the intermediate focal plane we need. In order to build this ray tracing properly we calculate the following parameters~:
\begin{eqnarray}
	F\#_\text{input} = \frac{\overline{\text{ExP-FP}}}{\diameter_{\text{ExtP}}}\nonumber\\
	F\#_\text{output} = \frac{f_\text{lens}}{\diameter_\text{beam on the lens}}\nonumber\\
	\gamma_\text{input} = \frac{1}{2F\#_\text{input}}\nonumber\\
	\gamma_\text{output} = \frac{1}{2F\#_\text{output}}\nonumber
\end{eqnarray}
The image of the pupil is nearby the foci (at 0.06~mm) and its raius has to be 5~mm. Taking the angles and the beam diameter on the TT modulation mirror we find the focal length of the lens and the distance from the intermediate focal plane described figure~\ref{fig:SW_trace_rayons_lens_TTMM}.
\begin{figure}[H]
	\begin{center}
		
		\caption{Ray tracing using SolidWorks to approximate the converging lens before the TT modulation mirror}\label{fig:SW_trace_rayons_lens_TTMM}
	\end{center}
\end{figure}
The focal length is rounded to $f~=~140$~mm. We introduce these results in Zemax using a paraxial lens (figure~\ref{fig:Zemax_model_FP_TTmod_noTilt}). We use the optimization tool to find the best focal plane (distance and radius of curvature at the image plane). We can see that the beam diameter on the TT modulation mirror surface is about 5~mm as expected. Taking a distance from the intermediate focal plane to the lens of 173~mm and the beam footprint diameter on the paraxial lens (on-axis case) we have a F\#$~=~\frac{136.58+597.36}{6.0897*2}~=~60.2$ which is larger than the F\#fixed before at 60.

\begin{figure}[H]
	\begin{center}
		
		\caption{Zemax model from the telescope beam to the TT modulation mirror using a paraxial lens}\label{fig:Zemax_model_FP_TTmod_noTilt}
	\end{center}
\end{figure}

In order to correct for the atmospheric chromatic dispersion we need to introduce an ADC (Atmospheric Dispersion Compensator, see~\ref{subsec:ADC}) in our system. This one has to be as close as possible to a pupil plane so to avoid to reimage the pupil and add optical surfaces we choose to insert it arount the TT modulation mirror. For now, we have placed the ADC in the design but it is only made of air. It is just here to have an idea of its size and the room we need for it arount the TT modulation mirror (see figure~\ref{fig:Zemax_model_FP_ApexPyr}).\\

We want to tilt the TT modulation mirror to send the beam in a convenient direction. Moreover we want to add the ADC around it so we can tilt the TT modulation mirror with an angle of about 20\degree. The diameter of the beam footprint on the TT modulation mirror (tilted to 20\degree) measured on the Zemax model is~10.63~mm (figure~\ref{fig:Zemax_model_FP_ApexPyr}) at maximum (which is smaller than 0.5~inch).\\

\begin{figure}[H]
	\begin{center}
		
		\caption{Zemax model from the telescope beam to the apex of the pyramid WFS.}\label{fig:Zemax_model_FP_ApexPyr}
	\end{center}
\end{figure}

\hl{Actually, we could play with the angle of the TT modulation mirror to place the ADC closer to the pupil plane. This would be investigate according to the ADC design.}

\subsection{Imaging the pupil on the CCD detector}\label{subsec:4eme_partie}
The detector is the Nuvu EMCCD with 128$^2$~pixels and a pixel size of $24~\mu$m. We have to sample the beam with at least 1 pixel per actuator. In order to relax the alignment specifications we can oversample the beam. According to Jean-Pierre Veran advice an oversampling of 1.5 should be enough. The ALPAO DM-468 has 22 actuators pitchs across the clear aperture diameter (so 23 actuators). Then we can calculate the beam diameter on the detector :
\begin{eqnarray}
	\diameter_{\text{CCD}} &= &\#_{\text{actuator across \diameter}}\times \text{PxSize}\times\text{Oversampling factor}\\
	\diameter_{\text{CCD}} &= &22\times 24~\mu\text{m}\times 1.5\\
	\diameter_{\text{CCD}} &= &0.792\,\,\text{mm}
\end{eqnarray}

The pupil has to be imaged on the camera through a relay lens. The pyramid does not act for the ray tracing and so the optical design, it separates the beam in four images only. We can look for the on-axis rays to dimension the relay lens and its position.\\
In order to play with the variables and have a direct result of what could be done or not, we used a sketch on the drawing software SolidWorks (figure~\ref{fig:SW_trace_rayons_TTMM_CCD}). Then, when we find something roughly fine we introduce the values in Zemax and optimize the distances in order to find the proper pupil plane and diameter.
\begin{figure}[H]
	\begin{center}
		
		\caption{SolidWorks ray tracing from the TT modulation mirror to the CCD.}\label{fig:SW_trace_rayons_TTMM_CCD}
	\end{center}
\end{figure}
We choose to fix the lens focal length in order to have a feasible lens. Playing with this distance we found that a lens of f~=~60~mm would be our best choice. We have changed the distance between the pyramid apex and the lens from 181~mm (according to figure~\ref{fig:SW_trace_rayons_TTMM_CCD}) to 213.615~mm to adjust for the pupil diameter. The distance from the lens to the CCD detector is fixed by the pupil position solver in Zemax. We can see figure~\ref{fig:Zemax_model_FP_CCD} that at the pupil plane, the pupil image has a diameter of $2*0.396~=~0.792$~mm as expected.
\begin{figure}[H]
	\begin{center}
		
		\caption{Zemax model of the bench until the CCD camera}\label{fig:Zemax_model_FP_CCD}
	\end{center}
\end{figure}

The natural guide star selection in the FoV is made using a XYZ stage where the WFS path is mounted. The TT modulation mirror is on a pupil plane so it can modulate the beam around the apex of the pyramid irrespectively of the star position. However, the pyramid has to be placed at the star focus in the FoV. The XY stage allows the NGS selection while the Z axis allows realigning the pupil when needed.

\subsection{The entire design}
Here is the entire design of the AO system.
\begin{figure}[H]
	\begin{center}
		
		\caption{Zemax model of the entire optical train}\label{fig:Entire_Design}
	\end{center}
\end{figure}

\subsection{Aberrations}
The AO optical model on Zemax shows that if the alignment and optical surfaces are ideals we should have a total amount of aberration less than 1 nm (largely dominated by spherical aberrations). However, we know that it is not going to be the case and some tolerance analyses are on process to give a realistic approximation of the system aberrations.
\begin{figure}[H]
	\begin{center}
		
		\caption{Wavefront and Zernike coefficients at the pyramid apex focal plane.}\label{fig:WF_aberrations}
	\end{center}
\end{figure}

\subsection{Atmopsheric Dispersion Compensator (ADC)}\label{subsec:ADC}
We are designing an ADC to compensate the atmospheric dispersion (see appendix\ref{app:ADC}). The geometric parameters and the glass are not set yet this is why we do not have implemented it in the Zemax model for now.

\subsection{Further development and optimization}
The current design will be completed with the optimized ADC, real lens models, the pyramid double prisms and an optional neutral density filter placed nearby the dichroic membrane to protect the camera for the bright stars.\\
This design could be slightly modified in order to update it to a GLAO (Ground Layer Adaptive Optics) system. We could add a beam splitter before the PWFS shoe box and duplicate this PWFS.

\newpage
% BIBLIOGRAPHIE
\bibliographystyle{ieeetr}
\renewcommand{\bibname}{References}
\bibliography{refbib/references_20180227_AO_design_report}
\addcontentsline {toc}{chapter}{References}
\addcontentsline {toc}{chapter}{Appendix}
\input{appendix/appendixes.tex}

\end{document}

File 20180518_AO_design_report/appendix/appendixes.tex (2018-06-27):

\appendix
\newpage
\section{OAPs focal lengths relations}\label{sec:EFL2PFL}
This section describe the relation between the parental and the effective focal length for an off-axis parabola. The sketch figure~\ref{fig:EFL2PFL_sketch} describes the situation with :
\begin{itemize}
	\item EFL the effective focal length
	\item PFL the parental focal length
	\item ($x_S, y_S$) the coordinate of the ray intersection with the parabola
	\item the parabola of equation \begin{equation}
	y = \frac{x^2}{4\text{PFL}}-\text{PFL}	\label{eq:parabola_general}
\end{equation}	 
\end{itemize}

\begin{figure}[H]
	\begin{center}
		
		\caption{Sketch of a ray reflected on an OAP}\label{fig:EFL2PFL_sketch}
	\end{center}
\end{figure}
The relation between EFL and PFL can be determined with the following set of equations.
\begin{eqnarray}
	x_S &= &\text{EFL}\sin\theta \nonumber\\
	y_S &= &\text{EFL}\cos\theta \label{eq:xs_ys}
\end{eqnarray}

Using \eqref{eq:parabola_general} and \eqref{eq:xs_ys} we have~:
\begin{eqnarray}
	4\text{PFL}\left(y_S+\text{PFL}\right) &= &x_S^2 \nonumber \\
	4\text{PFL}\left(\text{EFL}\cos\theta+\text{PFL}\right) &= &\left(\text{EFL}\sin\theta\right)^2\nonumber\\ 
	4\text{PFL}^2 - 4\text{PFL}\,\text{EFL}\cos\theta-\text{EFL}^2\sin^2\theta &= &0 \nonumber
\end{eqnarray}
\begin{eqnarray}
	\text{PFL}_{1,2} &= &\frac{4\text{EFL}\cos\theta\pm\sqrt{\left(-4\text{EFL}\cos\theta\right)^2+16\text{EFL}^2\sin^2\theta}}{2*4}  \nonumber\\
	&= &\frac{1}{2}\left[\text{EFL}\cos\theta\pm\sqrt{\text{EFL}^2\cos^2\theta+\text{EFL}^2\sin^2\theta}\right] \nonumber
\end{eqnarray}
The final equation is :
\begin{equation}
	2\text{PFL} = \text{EFL}\left(1+\cos\theta\right)\label{eq:EFL2PFL}
\end{equation}

%\newpage
%\section{Focal length of the relay lens between the pyramid and the CCD}\label{sec:PYR2CCD}
%Gauss :
%\begin{eqnarray}
%	\frac{1}{p_i}-\frac{1}{p_o} &= &\frac{1}{f_{LR}}	\nonumber\\
%	1-\frac{f_{LR}}{p_i} &= &-\frac{f_{LR}}{p_o}\label{eq:gaussPyr}
%\end{eqnarray}
%Thales :
%\begin{eqnarray}
%	\frac{\diameter_\text{CCD}}{\diameter_\text{L}} &= &\frac{|p_i|-|f_{LR}|}{|p_i|}\nonumber\\
%	\frac{\diameter_\text{CCD}}{\diameter_\text{L}} &= &1-\frac{f_{LR}}{p_i}\label{eq:ThalesPyr}
%\end{eqnarray}
%Mixing~\eqref{eq:gaussPyr} and \eqref{eq:ThalesPyr} :
%\begin{equation}
%	\frac{\diameter_\text{CCD}}{\diameter_\text{L}} = \frac{f_{LR}}{p_o}\label{eq:ThalGaussPyr}
%\end{equation}
%In another hand :
%\begin{equation}
%	\text{F}\# = \frac{f_\text{OAP3}}{\diameter_\text{TT}} = \frac{p_o}{\diameter_L}\label{eq:FnumPyr}
%\end{equation}
%Mixing \eqref{eq:ThalGaussPyr} and \eqref{eq:FnumPyr} :
%\begin{equation}
%f_\text{LR} = \text{F}\#\,\,\diameter_\text{CCD}
%\end{equation}

\newpage
\section{ADC design}\label{app:ADC}
\subsection{Scope}
The previous report explains the different possibilities to configure an ADC. Here we are presenting the design we are going to implement for the case of the DAG telescope AO. This ADC will be for visible wavelength. The range is limited by the camera Nuvu spectral range and the star spectrum studied. We are taking only the Nuvu camera bandwidth into account for a first iteration (500~nm to 900~nm).\\

\subsection{Amici principle}
As said in the previous report, the Amici prisms are commonly used in the ADC systems. The ADCs are composed by a 2-doublet design which mixes two Amici prisms. This kind of prism is an alliance of two pieces of glass which have different dispersion (different refractive indexes). The materials must have the same refractive number for a mean wavelength so that at this frequency the incident and emergent rays are parallel (zero-deviation at $\lambda_{av}$). The two prisms can be rotated around the optical axis in order to change the dispersion and compensate it for each zenith angle. When the angle between them is 180° the dispersion is reduced at its minimum.

\begin{figure}[H]
\centering
	
	\caption{2-doublet Amici prisms design}
	\centering
\end{figure}

Another design can be a three-glass Amici prisms, which is called triplet-design. It consists of the insertion of a anomalous dispersion glass between the two firstly introduced surfaces. According to Kopon thesis\cite{KCG}, the doublet corrects only the first order of chromatism while the triplet acts on both primary and secondary chromaticism aberration.
\begin{figure}[H]
\centering
	
	\caption{2-triplet Amici prisms design \cite{KCG}}
	\centering
\end{figure}

The triplet-design seems to be appropriate for our case because it gives the best performance. However, its cost (time to design it + manufacture) is much higher than the gain we can have adding one wedge in our Amici prism. This is why we are going to design a doublet prisms ADC.\\

The system is made only by plane surfaces so that a plane front which go through the prisms should leave them as a plane front. In a collimated beam with a very narrow field of view the prisms combined thickness can be larger than the beam diameter \cite{Wynne1992}.\\
We can also use vertex with a certain radius in a converging beam. This way we can change the F\# leaving the ADC.\\
The doublet glass has to be designed in order to have a thermal expansion rate as close as possible between each glass to not break with the temperature changes. The internal reflection is also a parameter that we have to take into account because we want the ADC to transmit as much as possible light.\\

In order to design our ADC, we need to collect some information about its position in the AO bench,the dispersion of the atmosphere for our parameters, the field of view (FoV) and wavelength bandwidth it has to work in.

\subsection{Model of the atmosphere chromatic dispersion}

The atmosphere chromatic dispersion can be computed looking at the refraction index for each interesting wavelength. The following model has been implemented in order to decide which dispersion the ADC has to compensate for.

\subsubsection{Atmosphere refraction index}
First, we need to model to atsmophere dispersion (refractive index) depending on the wavelength. The simulation of the atmosphere refractive index is based on Ciddor's approach \cite{Ciddor} which is a compilation of all previous equations for the visible and near infrared. Ciddor develops a process that we can easily follow in order to model correctly the atmosphere refractive index represented by :
\begin{equation}
	n_{final} = \left(\rho_a / \rho_{axs}\right)\left(n_{axs}-1\right)+\left(\rho_\omega / \rho_{\omega s}\right)\left(n_{\omega s}-1\right)\label{eq:Ciddor_nprop}
\end{equation}
The procedure to arrive to equation~\eqref{eq:Ciddor_nprop} is described by the following sections.\\

\textbf{\underline{Point 1:} svp, $f$, $x_w$}\\
\textbf{Saturated water vapour pressure in the humid air svp}\\
\begin{equation}
	\text{svp} = \exp\left(AT^2+BT +C+\frac{D}{T}\right)\,\,\,\,\,\text{[Pa]}\label{eq:svp}
\end{equation}
With the coefficients : $A = 1.2378847\times 10^{-5}$ [K$^{-2}$], $B = -1.9121316\times 10^{-2}$ [K$^{-1}$], $C = 33.93711047$ [-], $D = -6.4341645\times 10^3$ [K])

\textbf{Enhancement factor $f$ of water vapour in the air}\\
The molar mass of dry air containing $x_\text{CO2}$ ppm of CO2~:
\begin{equation}
	M_a = \left(28.9635+12.011\times 10^{^-6}(x_\text{CO2}-400)\right)\times 10^{^-3}\,\,\,\,\,\text{[kg/mol]}\label{eq:Ma}
\end{equation}
Here we take $x_\text{CO2} = 400$ [ppm].\\
The total pressure P :
\begin{equation}
	P = P_0\left(1-\frac{\Delta T\,H}{T}\right)^{\frac{g\,M_a}{R\Delta T}}\,\,\,\,\,\text{[Pa]}\label{eq:P}
\end{equation}
With $\Delta T~=~0.0065$~[K/100 m] the vertical gradient of temperature 0.65~K for 100~m in the troposphere\cite{app:wiki_troposphere}, $H$~[m] the altitude of the site (3170~m for Karakaya), $g~=~9.80665$~[m/s$^2$] the  earth-surface gravitational acceleration and $R~=~8.314510$~[J/mol/K] the universal gas constant.
The enhancement factor :
\begin{equation}
	f = \alpha+\beta P+\gamma T^2 
\end{equation}
With $\alpha = 1.00062$~[-], $\beta  = 3.14\times 10^{-8}$~[Pa$^-1$], $\gamma = 5.6\times 10^{-7}$~[°C$^{-2}$]

\textbf{Molar fraction of water vapor in moist air $x_w$}\\
\begin{equation}
	x_w = \text{RH}\,f\frac{\text{svp}}{P} 
\end{equation}
With RH the relative humidity (RH~=~0.8 for DAG).\\

\textbf{\underline{Point 2:} n$_\text{axs}$}\\
Constants involved in the standard phase and group refractivities of dry air $k_0~=~238.0185$, $k_1~=~5792105$, $k_2~=~57.362$, $k_3~=~167917\,[\mu $m$^{-2}]$.\\
The refractive index of standard air at T=20\degree C, 101325 Pa, 0 \% humidity, 450 ppm of CO$_2$~:
\begin{equation}
	10^8 \left(n_{as}-1\right) = k_1/\left(k_0-\sigma ^2\right)+k_3/\left(k_2-\sigma ^2\right)\label{eq:naxs}
\end{equation}
With $\sigma  = 1/\lambda\,\,[\mu $m$^{^-1}]$. 
For us it is not useful to have the following equation because we are in a standard case so $n_{axs}~=~n_{as}$, but I let it in order to remember the sequence of equations :
\begin{equation}
	\left(n_{axs}-1\right) = \left(n_{as}-1\right) \left[1+0.534\times 10^{^-6}\left(x_c-450\right)\right] \label{eq:nasx}
\end{equation}
With $x_c~=~450$ [-ppm] number of ppm of CO2 (standard).\\

\textbf{\underline{Point 3:} $M_a$} see equation~\eqref{eq:Ma}.\\

\textbf{\underline{Point 4:} $Z_a$}\\
The compressibility of dry air :
\begin{equation}
	Z_\text{as} = 1-\frac{P_\text{as}}{T_\text{as}}\left[a_0+a_1\,T_\text{as}+a_2\,T_\text{as}^2+\left(b_0+b_1\,T_\text{as}\right)*x_{w\text{as}} +(c_0+c_1\,T_\text{as})*x_{w\text{as}}^2\right] +\frac{P_\text{as}^2}{T_\text{as}^2}\left(d+e*x_{w\text{as}}^2\right)\label{eq:Za}
\end{equation}
With $x_{w\text{as}}~=~0$ the molar fraction of water vapor in moist air (here we are in dry air so~0), $P_\text{as}$ [Pa] the pressure, $T_\text{as}$ [K] temperature at standard conditions and the following coefficients the compressibility factor Z~: 
\begin{multicols}{3}
$a_0~=~1.58123\times~10^{-6}\,[$K*Pa$^{-1}]$,\\
$a_1~=~-2.9331\times~10^{-8}\,[$P$a^{-1}]$,\\
$a_2~=~1.1043\times~10^{-10}\,[$(KPa)$^{-1}]$,\\
$b_0~=~5.707\times~10^{-6}\,[$K*Pa$^{-1}]$,\\
$b_1~=~-2.051\times~10^{-8}\,[$Pa$^{-1}]$,\\
$c_0~=~1.9898\times~10^{-4}\,[$K*Pa$^{-1}]$,\\
$c_1~=~-2.376\times~10^{-6}\,[$Pa$^{-1}]$,\\
$d~=~1.83\times~10^{-11}\,[$K$^2$Pa$^{-2}]$,\\
$e~=~-0.765\times~10^{-8}\,[$K$^2$Pa$^{-2}]$
\end{multicols}

\textbf{\underline{Point 5:} $Z_w$}\\
The compressibility of pure water vapour :
\begin{equation}
	Z_\text{ws} = 1-\frac{P_\text{ws}}{T_\text{ws}}\left[a_0+a_1\,T_\text{ws}+a_2\,T_\text{ws}^2+\left(b_0+b_1\,T_\text{ws}\right)*x_{w\text{ws}} +(c_0+c_1\,T_\text{ws})*x_{w\text{ws}}^2\right] +\frac{P_\text{ws}^2}{T_\text{ws}^2}\left(d+e*x_{w\text{ws}}^2\right)\label{eq:Zw}
\end{equation}
With $x_{w\text{ws}}~=~1$ the molar fraction of water vapor in moist air (here we are in moist air so~1), $P_\text{ws}~=~1333$ [Pa] the pressure, $T_\text{ws}~=~293.15$ [K] the temperature.\\

\textbf{\underline{Point 6:} $\rho_\text{axs}, \rho_\text{ws}$}\\
The density of standard dry air [kg/m$^3$]~:
\begin{equation}
	\rho_\text{axs} = \frac{P_\text{as}\,M_a}{Z_\text{as}\,R\,T_\text{as}}\left(1-x_{w\text{as}}\left(1-\frac{M_w}{M_a}\right)\right)
\end{equation}
The density of standard moist air [kg/m$^3$]~:
\begin{equation}
	\rho_\text{ws} = \frac{P_\text{ws}\,M_a}{Z_\text{ws}\,R\,T_\text{ws}}\left(1-x_{w\text{ws}}\left(1-\frac{M_w}{M_a}\right)\right)
\end{equation}
With $M_w~=~18.01528\times10^{-3}$ [kg/mol].\\

\textbf{\underline{Point 7:} $Z$}\\
The compressibility of moist air under experimental conditions~:
\begin{equation}
	Z = 1-\frac{P_\text{w}}{T_\text{w}}\left[a_0+a_1\,T_\text{w}+a_2\,T_\text{w}^2+\left(b_0+b_1\,T_\text{w}\right)*x_{w\text{w}} +(c_0+c_1\,T_\text{w})*x_{w\text{w}}^2\right] +\frac{P_\text{w}^2}{T_\text{w}^2}\left(d+e*x_{w\text{w}}^2\right)\label{eq:Zw}
\end{equation}

\textbf{\underline{Point 8:} $\rho_a$}\\
The density of the dry component of the moist air [kg/m$^3$]~:
\begin{equation}
	\rho_a = P\,Ma\frac{\left(1-x_a\right)}{Z\,R\,T_a}\label{eq:rho_a}
\end{equation}

\textbf{\underline{Point 9:} $\rho_w$}\\
The density of the dry component of the moist air [kg/m$^3$]~:
\begin{equation}
	\rho_a = P\,Ma\frac{\left(1-x_a\right)}{Z\,R\,T_a}\label{eq:rho_a}
\end{equation}

\textbf{\underline{Point 10:} $n_{final}$}\\
Constants involved in the standard phase and group refractivities of water vapour~:\\
$\omega_0 = 295.235\,[\mu $m$^{-2}],\,\,\omega_1 = 2.6422\,[\mu $m$^{-2}],\,\,\omega_2 = -0.032380\,[\mu $m$^{-4}],\,\,\omega_3 = 0.004028\,[\mu$m$^{-6}]$.\\
The refractive index of water vapour at 20°C, 1335Pa~:
\begin{equation}
	10^8 \left(n_{ws}-1\right) = 1.022\times\left(\omega_0+\omega_1\sigma^2+\omega_2\sigma^4+\omega_3\sigma^6\right)
\end{equation}

The refractive index of moist air (atmosphere)~:
\begin{equation}
	n_{final} = \left(\rho_a / \rho_{axs}\right)\left(n_{axs}-1\right)+\left(\rho_\omega / \rho_{\omega s}\right)\left(n_{\omega s}-1\right)\label{eq:Ciddor_nprop}
\end{equation}

\subsubsection{Atmosphere refraction equation}
The refraction of the atmosphere is computed with the equation \cite{Stone1996}: 
\begin{equation}
	R(\lambda,z) = \kappa\left(n(\lambda)-1\right)\left(1-\beta\right)\tan(z) - \kappa\left(n(\lambda)-1\right)\left(\beta -\frac{\left(n(\lambda)-1\right)}{2}\right)\tan^3(z)\,\,\,[\text{rad}]\label{eq:Ratm}
\end{equation}
with 
\begin{itemize}
	\item $\beta = 0.001254\left(\frac{T(K)}{273.15}\right)$ the effective height of the observatory above the surface of the earth \cite{Stone1996}
	\item $\kappa = 1$ for a spherical Earth surface \cite{Stone1996} or instrumental correction no more useful \cite{Stone2002}
\end{itemize} 
This equation~\eqref{eq:Ratm} is valid only for zenith angle $<$ 75\degree. We can even neglect the second term for zenith angles $<$ 65\degree \cite{Tendulkar}. The limit of zenith angle of our computation is set to 70\degree so the entire equation is set.\\

The model applied for the wavelength range [500, 900]~nm shows~:
\begin{figure}[H]
\centering
	
	\caption{Angular dispersion of the atmosphere~(appendix~\ref{app:test_Refraction_atmosphere})}\label{fig:refraction_atm}
	\centering
\end{figure}

\subsubsection{Wavelength range}
For our case, the wavelength range is set by the Nuvu camera~\cite{NuvuQE} bandwidth limits $\lambda_{min} = 500$~[nm] and $\lambda_{max} = 900$~[nm] and the maximum quantum efficiency that fixes the central wavelength to $\lambda_{cen} = 600$~[nm]. We use these 3 reference wavelengths to compute the ADC efficiency.

\subsubsection{Glasses for the ADC}
The choice of glass depends on the range of zenith angles, the wavelength interval and the cost \cite{WynneWors1986}. Most of the glass couple in the Amici conception are flint/crown pairs. \\
The glass choice is made in a data base built from Schott and Ohara catalogues. The data are taken from~\cite{RefIndexInfo} where we can download glasses properties from many different suppliers. The data are sorted to extract Sellmeier coefficients~\cite{SchottSellmeier} in order to compute the refractive index of each glass depending on the wavelength with the equation~\eqref{eq:Sellmeier}.

\begin{equation}
	n^2(\lambda) = 1+ \frac{B_1\lambda^2}{\lambda^2-C_1}+\frac{B_2\lambda^2}{\lambda^2-C_2}+\frac{B_3\lambda^2}{\lambda^2-C_3}\label{eq:Sellmeier}
\end{equation}
with $B_i$ and $C_i$ Sellmeier coefficients for $\lambda$ in $\mu$m~\cite{SchottSellmeier}.\\

\subsubsection{Beam propagation through the ADC}
In order to compute de dispersion through the ADC a geometrical and refraction set of equations have been implemented. The sequence of these equations is listed bellow. I will follow the light on the figure~\ref{fig:ADCgeometrie} to describe each step.
\begin{figure}[H]
\centering
	
	\caption{Sketch of the refraction through the ADC}\label{fig:ADCgeometrie}
	\centering
\end{figure}
The refractive index of the I-th glass is $n_I(\lambda_i)$. To simplify the notation, we just write $n_I$.
We apply the sign convention described in the course material~\cite{coursOptLJT}.

The function \textit{exitAngle.py}~\ref{app:modelisationADCfunctions} computes the exit angle depending on the glass refractive index, the geometrical parameters of the prisms and the entrance angle.\\

%
%
%\paragraph*{At the entrance we have the vector}
%$\begin{bmatrix}x_E \\ z_E = 0 \\ n_0\sin\alpha_E\end{bmatrix}$
% 
%\paragraph*{At the entrance 0E, we have a refraction}
%$\begin{bmatrix}x_E \\ z_E = 0 \\ n_A\sin\alpha_1\end{bmatrix}$\\
%
%which gives :\\
%
%$\alpha_1 = \arcsin\left(\frac{n_0}{n_A}\sin\alpha_E\right) $
%
%\paragraph*{At the first interface AB, we arrive with the coordinates}
%
%$\begin{bmatrix}x_A \\ z_A \\ n_A\sin\left(\alpha_2\right)\end{bmatrix}$
%\begin{figure}[H]
%\centering
%	\includegraphics[width = .3\textwidth]{images/triangleGeo.png}
%	\caption{Decomposition of the parameters at an interface}\label{fig:triangle}
%	\centering
%\end{figure}
%We can determine this vector using the following equations from figure~\ref{fig:triangle} :\\
%
%$X = \frac{d_A}{\tan\theta_A}$ ; $\frac{X-x_A}{X} = \frac{z_A}{d_A}$ ; $z_A = \frac{x_E-x_A}{\tan\alpha_1}$\\
%
%Then we find :\\
%$\left \{
%   \begin{array}{r c l}
%      x_A  & = & \frac{x_E-d_A\tan\alpha_1}{1-\tan\alpha_1\tan\theta_A} \\
%      z_A   & = & \frac{x_E-x_A}{\tan\alpha1} \\
%      \alpha_2 & = & \alpha_1+\theta_A
%   \end{array}
%\right.$
%
%\paragraph*{At the interface AB, we have a refraction}
%$\begin{bmatrix}x_A \\ z_A \\ n_B\sin\alpha_3\end{bmatrix}$\\
%
%which gives :\\
%
%$\alpha_3 = \arcsin\left(\frac{n_A}{n_B}\sin\alpha_2\right) $
%
%\paragraph*{At the interface BC, we arrive with the coordinates}
%
%$\begin{bmatrix}x_B \\ z_B \\ n_B\sin\left(\alpha_4\right)\end{bmatrix}$\\
%
%We can determine this vector using the following equations from figure~\ref{fig:triangle} :\\
%
%$X = \frac{x_A}{\tan\alpha_A}$ ; $\frac{x_B}{X-Q-d_B+m} = \tan\alpha_A$ ; $m = d_A+d_B-z_B$ ; $m = x_B\tan\theta_B$ ; $Q = d_A-z_A$ ; $\alpha_A = \alpha_3+\theta_A$\\
%
%Then we find :\\
%$\left \{
%   \begin{array}{r c l}
%      x_B  & = & \frac{x_A-\tan\alpha_A\left(d_A+d_B-z_A\right)}{1-\tan\alpha_A\tan\theta_B} \\
%      z_B   & = & d_A+d_B-x_B\tan\theta_B \\
%      \alpha_4 & = & \alpha_A+\theta_B
%   \end{array}
%\right.$
%
%\paragraph*{At the interface BC, we have a refraction}
%$\begin{bmatrix}x_B \\ z_B \\ n_C\sin\alpha_5\end{bmatrix}$\\
%
%which gives :\\
%
%$\alpha_5 = \arcsin\left(\frac{n_B}{n_C}\sin\alpha_4\right) $
%
%
%\paragraph*{At the interface C0, we arrive with the coordinates}
%
%$\begin{bmatrix}x_C \\ z_C \\ n_C\sin\left(\alpha_6\right)\end{bmatrix}$\\
%
%We can determine this vector using the following equations from figure~\ref{fig:triangle} :\\
%
%$X = \frac{x_B}{\tan\alpha_B}$ ; $\frac{x_C}{X-Q-d_C+m} = \tan\alpha_B$ ; $m = d_A+d_B-z_B$ ; $m = x_C\tan\theta_C$ ; $Q = d_A+d_B-z_B$ ; $\alpha_B = \alpha_5+\theta_B$\\
%
%Then we find :\\
%$\left \{
%   \begin{array}{r c l}
%      x_C  & = & \frac{x_B-\tan\alpha_B\left(d_A+d_B+d_C-z_B\right)}{1-\tan\alpha_B\tan\theta_C} \\
%      z_B   & = & d_A+d_B+d_C-x_C\tan\theta_C \\
%      \alpha_6 & = & \alpha_B+\theta_C
%   \end{array}
%\right.$
%
%\paragraph*{At the interface C0, we have a refraction}
%$\begin{bmatrix}x_C \\ z_C \\ n_0\sin\alpha_7\end{bmatrix}$\\
%
%which gives :\\
%
%$\alpha_7 = \arcsin\left(\frac{n_C}{n_0}\sin\alpha_6\right) $\\
%
%\paragraph*{The output angle with respect to the optical axis}\
%$\alpha_S = \alpha_7-\theta_C$
%This $\alpha_S$ is the dispersion angle of the prism : $R_{prism} = \alpha_S$.
%

\subsubsection{The metric definition}
Now we have computed the dispersion of the atmosphere and the ADC. We want the smallest total dispersion after the ADC so we investigate all configurations in order to minimize it. The metric we use to calculate the efficiency of our prism combination~(appendix~\ref{app:glassChoice}) is defined by the name BDCQ (Beam Dispersion Correction Quality)~:
\begin{equation}
	\text{BDCQ}^2 = \left(\alpha_\text{Exit}\left(\lambda_{min}\right)-\alpha_\text{Exit}\left(\lambda_{av}\right)\right)^2 + \left(\alpha_\text{Exit}\left(\lambda_{max}\right)-\alpha_\text{Exit}\left(\lambda_{av}\right)\right)^2 +\\
	 \left(\alpha_\text{Exit}\left(\lambda_{av}\right)-\alpha_\text{Entry}\left(\lambda_{av}\right)\right)^2
\end{equation}

\subsubsection{Internal reflection}
In parallel of the dispersion computation, we calculate the total internal reflection of the ADC. If the refractive index of two joint glasses are too different then we will loose a lot of intensity reflected on the interface. The external faces of the ADC will be coated. The determination of the total internal reflectivity is developed below.\\
The parameters are :
\begin{itemize}
	\item $\alpha_Z = [\alpha_E;\alpha_1;\alpha_A;\alpha_B;\alpha_S]$ [rad] array of the rays angle wrt the optical axis
	\item $\alpha_I = [\alpha_1;\alpha_2;\alpha_3;\alpha_4;\alpha_5;\alpha_6;\alpha_7]$ [rad] array of the rays angles wrt the normal the vertex (refraction angle)
	\item $n = [n_0;n_A;n_B;n_C;n_0]$ medium refractive index
	\item $d = [z_A,z_B-z_A,z_C-z_B]$ [mm] distances on the optical axis between each medium change on the ray path
\end{itemize}

At the 1rst interface AB, we have~\cite{app:wiki_CoefficientsFresnel}:
\begin{equation}
	r[1] = \frac{n[3]\cos\alpha_I[2]-n[2]\cos\alpha_I[3]}{n[3]\cos\alpha_I[2]+n[2]\cos\alpha_I[3]}
\end{equation}
Taking the recursive initialization term $U(1) = r(1)$ we have for p = 2:\\
\begin{eqnarray}
	r[p] &= &\frac{n[p+1]\cos\left(\alpha_I[p]\right)-n[p]\cos\left(\alpha_I[p+1]\right)}{n[p+1]\cos\left(\alpha_I[p]\right)+n[p]\cos\left(\alpha_I[p+1]\right)}\\
	U[p] &= &\frac{U[p-1]+r[p]\exp\left(\frac{2\pi}{\lambda}\cos\left(\alpha_Z[p]\right)\,d[p-1]\right)}{1+U[p-1]\,r[p]\exp\left(\frac{2\pi}{\lambda}\cos\left(\alpha_Z[p]\right)\,d[p-1]\right)}\label{eq:Up}
\end{eqnarray}
Using equation~\eqref{eq:Up} we can calculate the reflection coefficient for $(p+1)$ number of glasses. In our case we have only 3 glasses so the total reflection (without taking external faces into account) is $U[2]$.

\subsection{ADC design optimization}
The efficiency of a combination (glass, angle) is computed by the script \textit{glassChoice.py}. The function \textit{fmin\_l\_bfgs\_b} from the optimize package in Python is used to find minimum of this constrained nonlinear multivariable function. The parameters are the geometrical coefficients for one set of glass. When the optimum is found for a combination of glass, the efficiency and internal reflection are given as outputs.\\

The global matrix is made from two for-loops that look for all glasses from the catalogues Schott and Ohara. The wavelength for which the refraction is calculated are taken from the Nuvu camera quantum efficiency curve~: $\lambda_\text{min}~=~500$ nm, $\lambda_\text{average}~=~600$ nm and $\lambda_\text{max}~=~900$ nm. The zenith angle is set to 70\degree.

\newpage
\section{DimensionnementOAPs.py}\label{app:DimensionnementOAPs}
\lstinputlisting[language=Python]{../DimensionnementOAPs.py}

\section{modelisationADCfunctions.py}\label{app:modelisationADCfunctions}
%\lstinputlisting[language=Python]{../20180611\_ADC\_design/modelisationADCfunctions.py}

\section{test\_Refraction\_atmosphere.py}\label{app:test_Refraction_atmosphere}
%\lstinputlisting[language=Python]{../20180611\_ADC\_design/test\_Refraction\_atmosphere.py}

\section{glassChoice.py}\label{app:glassChoice}
%\lstinputlisting[language=Python]{../20180611\_ADC\_design/glassChoice.py}

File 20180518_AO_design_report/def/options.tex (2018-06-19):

\usepackage{amsfonts}
\usepackage{amscd}
\usepackage{amsmath}
\usepackage{amssymb}
\usepackage[english]{babel}
\usepackage{cite}
\usepackage{enumitem}
\usepackage[12pt]{extsizes}
\usepackage{epstopdf}
\usepackage{fancyhdr}
\usepackage{geometry}
\usepackage{graphicx}
\usepackage[utf8x]{inputenc} % UTF-8
\usepackage{lmodern}
\usepackage{setspace}
\usepackage{tabularx}
\usepackage{textcomp}
\usepackage{threeparttable}
\usepackage{titlesec}
\usepackage{wrapfig}

\geometry{top=2.5cm, bottom=2.5cm, left=2.5cm, right=2.3cm}

\headheight = 130pt
\textheight = 590pt
\footskip = 1pt

\pagestyle{fancy}

\setlist[itemize]{noitemsep}
\onehalfspacing

\newcommand{\re}{\ensuremath{\mathcal{R}e}}
\newcommand{\im}{\ensuremath{\mathcal{I}m}}
\newcommand{\tf}{\ensuremath{\mathcal{F}}}

\usepackage{outlines}	% pour pouvoir subitemize et mettre des numéro à chaque points
\usepackage[export]{adjustbox} % to allow putting left/center/right command for figure

\usepackage{wasysym}
\usepackage{gensymb}
\usepackage{afterpage}
\usepackage{float} 
\usepackage{graphicx}
\usepackage{subcaption}
\usepackage{soul,color}

%Pour les codes en Python :
\usepackage{color}

\definecolor{mygreen}{rgb}{0,0.6,0}
\definecolor{mygray}{rgb}{0.5,0.5,0.5}
\definecolor{mymauve}{rgb}{0.58,0,0.82}
\usepackage{listings}
\lstset{ 
  backgroundcolor=\color{white},   % choose the background color; you must add \usepackage{color} or \usepackage{xcolor}; should come as last argument
  basicstyle=\footnotesize,        % the size of the fonts that are used for the code
  breakatwhitespace=false,         % sets if automatic breaks should only happen at whitespace
  breaklines=true,                 % sets automatic line breaking
  captionpos=b,                    % sets the caption-position to bottom
  commentstyle=\color{mygreen},    % comment style
  deletekeywords={...},            % if you want to delete keywords from the given language
  escapeinside={\%*}{*)},          % if you want to add LaTeX within your code
  extendedchars=true,              % lets you use non-ASCII characters; for 8-bits encodings only, does not work with UTF-8
  frame=single,	                   % adds a frame around the code
  keepspaces=true,                 % keeps spaces in text, useful for keeping indentation of code (possibly needs columns=flexible)
  keywordstyle=\color{blue},       % keyword style
  language=Octave,                 % the language of the code
  morekeywords={*,...},            % if you want to add more keywords to the set
  numbers=left,                    % where to put the line-numbers; possible values are (none, left, right)
  numbersep=5pt,                   % how far the line-numbers are from the code
  numberstyle=\tiny\color{mygray}, % the style that is used for the line-numbers
  rulecolor=\color{black},         % if not set, the frame-color may be changed on line-breaks within not-black text (e.g. comments (green here))
  showspaces=false,                % show spaces everywhere adding particular underscores; it overrides 'showstringspaces'
  showstringspaces=false,          % underline spaces within strings only
  showtabs=false,                  % show tabs within strings adding particular underscores
  stepnumber=2,                    % the step between two line-numbers. If it's 1, each line will be numbered
  stringstyle=\color{mymauve},     % string literal style
  tabsize=2,	                   % sets default tabsize to 2 spaces
  title=\lstname                   % show the filename of files included with \lstinputlisting; also try caption instead of title
}

\usepackage{multicol}

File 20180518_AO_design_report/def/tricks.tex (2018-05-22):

%% TRICKS

%%%%%%%%%%%%%%%%%%%%%%%%%%%%%%%%%%%%%%%%%%%%%%%%%%%%%%%%%%%%%%%%%

% Minipage 2 tabular

\begin{table}[!htb]
    \begin{minipage}{.5\linewidth}
      \centering
        \begin{tabular}{ll}
            1 & 2
        \end{tabular}
    \end{minipage}%
    \begin{minipage}{.5\linewidth}
      \centering
        \begin{tabular}{ll}
            3 & 4
        \end{tabular}
    \end{minipage}
    \caption{Global caption} 
\end{table}

%%%%%%%%%%%%%%%%%%%%%%%%%%%%%%%%%%%%%%%%%%%%%%%%%%%%%%%%%%%%%%%%%

% 1 FIGURE

\begin{figure}[!h]
	\begin{center}
		
		\caption{•}
		\label{•}
	\end{center}
\end{figure}

%%%%%%%%%%%%%%%%%%%%%%%%%%%%%%%%%%%%%%%%%%%%%%%%%%%%%%%%%%%%%%%%%

% 2 SUBFIGURE (in line)

\begin{figure}[!h]
	\begin{center}
		\subfigure[]{}
		\subfigure[]{}
		\caption{•}
		\label{•}
	\end{center}
\end{figure}

%%%%%%%%%%%%%%%%%%%%%%%%%%%%%%%%%%%%%%%%%%%%%%%%%%%%%%%%%%%%%%%%%

% 

\begin{figure}[!htb]
    \centering
    \begin{minipage}{.5\textwidth}
        \centering
        
        \caption{$dt=0.1$}
        \label{fig:prob1_6_2}
    \end{minipage}%
    \begin{minipage}{0.5\textwidth}
        \centering
        
        \caption{$dt =$}
        \label{fig:prob1_6_1}
    \end{minipage}
\end{figure}

%%%%%%%%%%%%%%%%%%%%%%%%%%%%%%%%%%%%%%%%%%%%%%%%%%%%%%%%%%%%%%%%%

% WarningPanel

\begin{figure}[!h]
	\begin{center}
		
	\end{center}
\end{figure}

%%%%%%%%%%%%%%%%%%%%%%%%%%%%%%%%%%%%%%%%%%%%%%%%%%%%%%%%%%%%%%%%%

% MaterialSelectionTable

\begin{table}[!h]
	\begin{center}
		\begin{tabular}{lll}
		\hline
		\textbf{Part} & \textbf{Material} & \textbf{Justification}\\
		\hline
		 &  & \\
		\hline
		 &  & \\
		\hline
		 &  & \\
		\hline
		 &  & \\
		\hline
		 &  & \\
		\hline
		 &  & \\
		\hline
		 &  & \\
		\hline
		\end{tabular}
		\caption{Material selection}
		\label{tab_materialSelectionTab01}
	\end{center}
\end{table}

%%%%%%%%%%%%%%%%%%%%%%%%%%%%%%%%%%%%%%%%%%%%%%%%%%%%%%%%%%%%%%%%%

% Material

\begin{table}[!h]
	\begin{center}
	\begin{tabular}{clc}
	\hline
	$E$ & $-$ &[N/mm$^2$]\\ 				% Young modulus
	\hline
	$\nu$ & $-$ & [-]\\						% Poisson's modulus
	\hline
	$G$ & $-$ & [N/mm$^2$]\\				% Shear modulus
	\hline
	$\rho$ & $-$ & [kg/m$^3$]\\				% Density
	\hline
	$R_m$ & $-$ & [N/mm$^2$]\\ 				% limite de traction
	\hline
	$R_{p0.2}$ & $-$ & [N/mm$^2$]\\ 		% = R_e = yield strength = \sigma_y
	\hline
	$\alpha$ & $-\cdot 10^{-6}$ & [K$^{-1}$]\\			% CTE $\cdot 10^{-6}$
	\hline
	$K$ & $-$ & [W/(m$\cdot$ K)]\\ 			% Thermal conductivity
	\hline
	$c$ & $-$ & [J/(kg $\cdot$ K)]\\		% Specific heat
	\hline
	\end{tabular}
	\caption{•} %\\ \scriptsize{Source: }
	\label{mat_}
	\end{center}
\end{table}

%%%%%%%%%%%%%%%%%%%%%%%%%%%%%%%%%%%%%%%%%%%%%%%%%%%%%%%%%%%%%%%%%

% Material tabular

	\begin{tabular}{clc}
	\hline
	$E$ & $-$ &[N/mm$^2$]\\ 				% Young modulus
	\hline
	$\nu$ & $-$ & [-]\\						% Poisson's modulus
	\hline
	$G$ & $-$ & [N/mm$^2$]\\				% Shear modulus
	\hline
	$\rho$ & $-$ & [kg/m$^3$]\\				% Density
	\hline
	$R_m$ & $-$ & [N/mm$^2$]\\ 				% limite de traction
	\hline
	$R_{p0.2}$ & $-$ & [N/mm$^2$]\\ 		% = R_e = yield strength = \sigma_y
	\hline
	$\alpha$ & $-\cdot 10^{-6}$ & [K$^{-1}$]\\			% CTE $\cdot 10^{-6}$
	\hline
	$K$ & $-$ & [W/(m$\cdot$ K)]\\ 			% Thermal conductivity
	\hline
	$c$ & $-$ & [J/(kg $\cdot$ K)]\\		% Specific heat
	\hline
	\end{tabular}
	\caption{•} %\\ \scriptsize{Source: }
	\label{mat_}

%%%%%%%%%%%%%%%%%%%%%%%%%%%%%%%%%%%%%%%%%%%%%%%%%%%%%%%%%%%%%%%%%

% 4 materials multiTable

\begin{table}[!htb]
	\centering
    \begin{minipage}{.32\linewidth}
      \centering
        \input{mat/mat_PYROFIL_MS_40_12M_tabular.tex}
    \end{minipage}
    \hspace{1cm}
    \begin{minipage}{.32\linewidth}
      \centering
        \input{mat/mat_InvarAC36_tabular.tex}
    \end{minipage}
    \\
    \vspace{1cm}
    \begin{minipage}{.32\linewidth}
      \centering
        \input{mat/mat_S235JRG2_tabular.tex}
    \end{minipage}
    \hspace{1cm}
    \begin{minipage}{.32\linewidth}
      \centering
        \input{mat/mat_S235JRG2_tabular.tex}
    \end{minipage}
    %\caption{}
    %\label{}
\end{table}

%%%%%%%%%%%%%%%%%%%%%%%%%%%%%%%%%%%%%%%%%%%%%%%%%%%%%%%%%%%%%%%%%

% TIKZ SCALEBOX
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

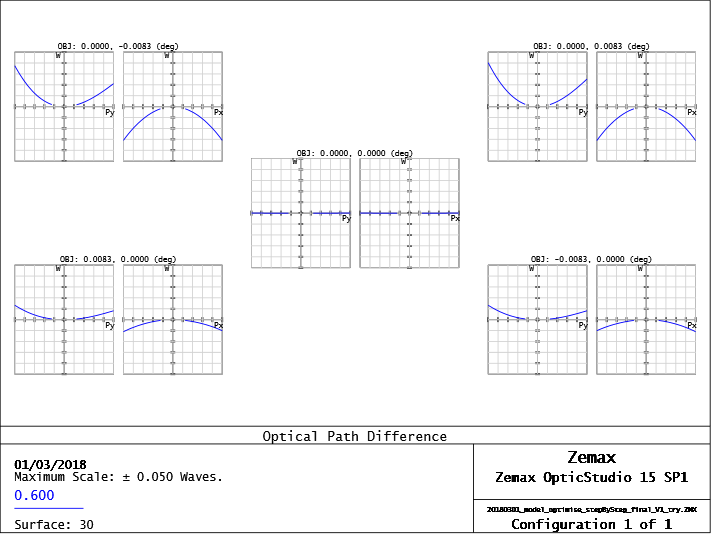
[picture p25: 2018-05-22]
20180518_AO_design_report/images/OPD_Fan_Intermediate_FP_2nd_approach.png

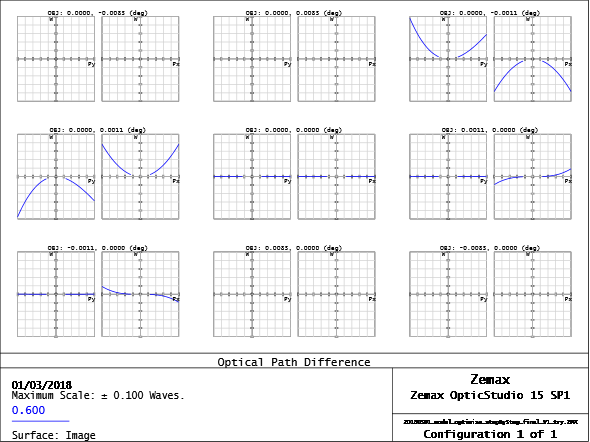
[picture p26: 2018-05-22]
20180518_AO_design_report/images/OPD_Fan_PyrApex_2nd_approach.png

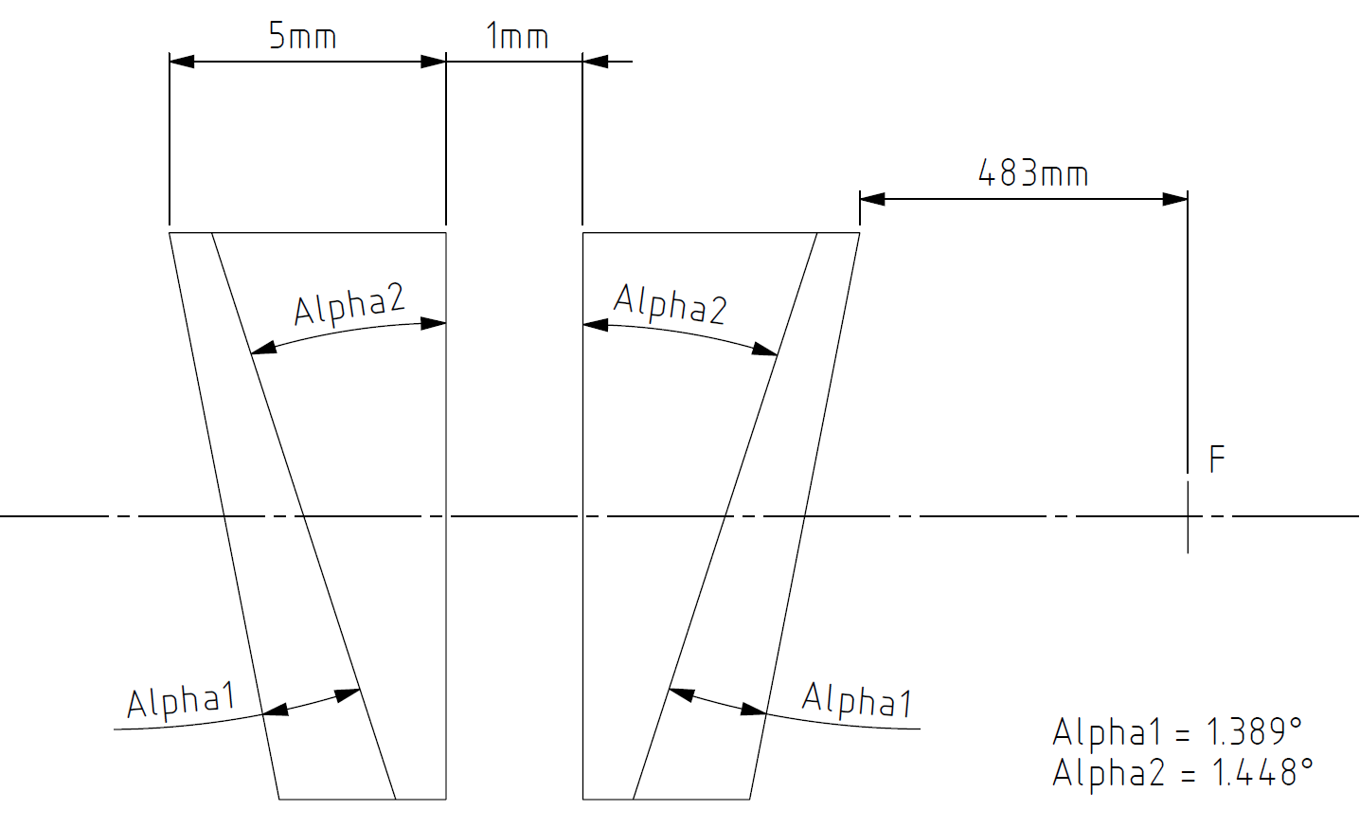
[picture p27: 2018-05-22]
20180518_AO_design_report/images/KeckADC.PNG

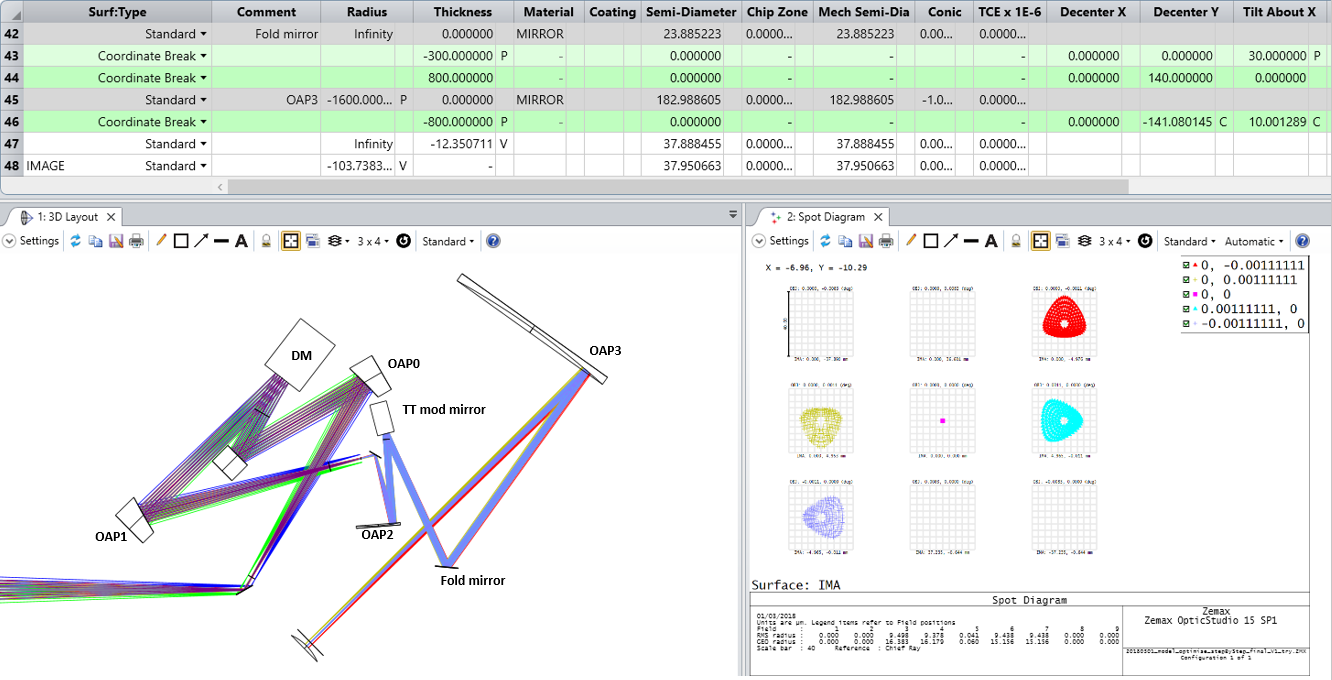
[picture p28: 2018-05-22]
20180518_AO_design_report/images/Zemax_model_FP_OAP3_fold_2nd_approach.PNG

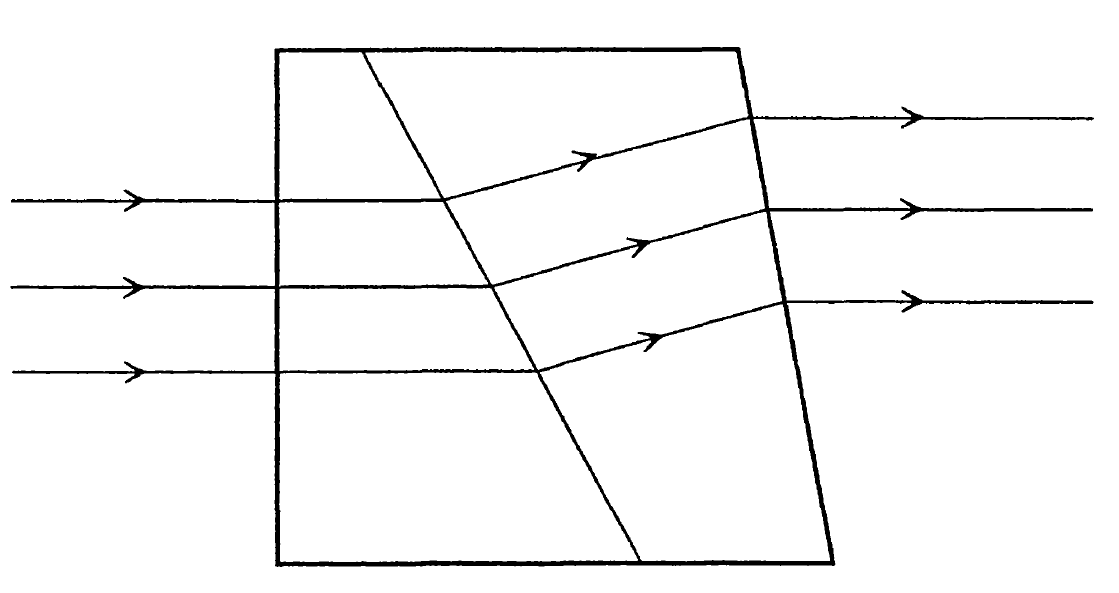
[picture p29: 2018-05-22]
20180518_AO_design_report/images/Amici1.PNG

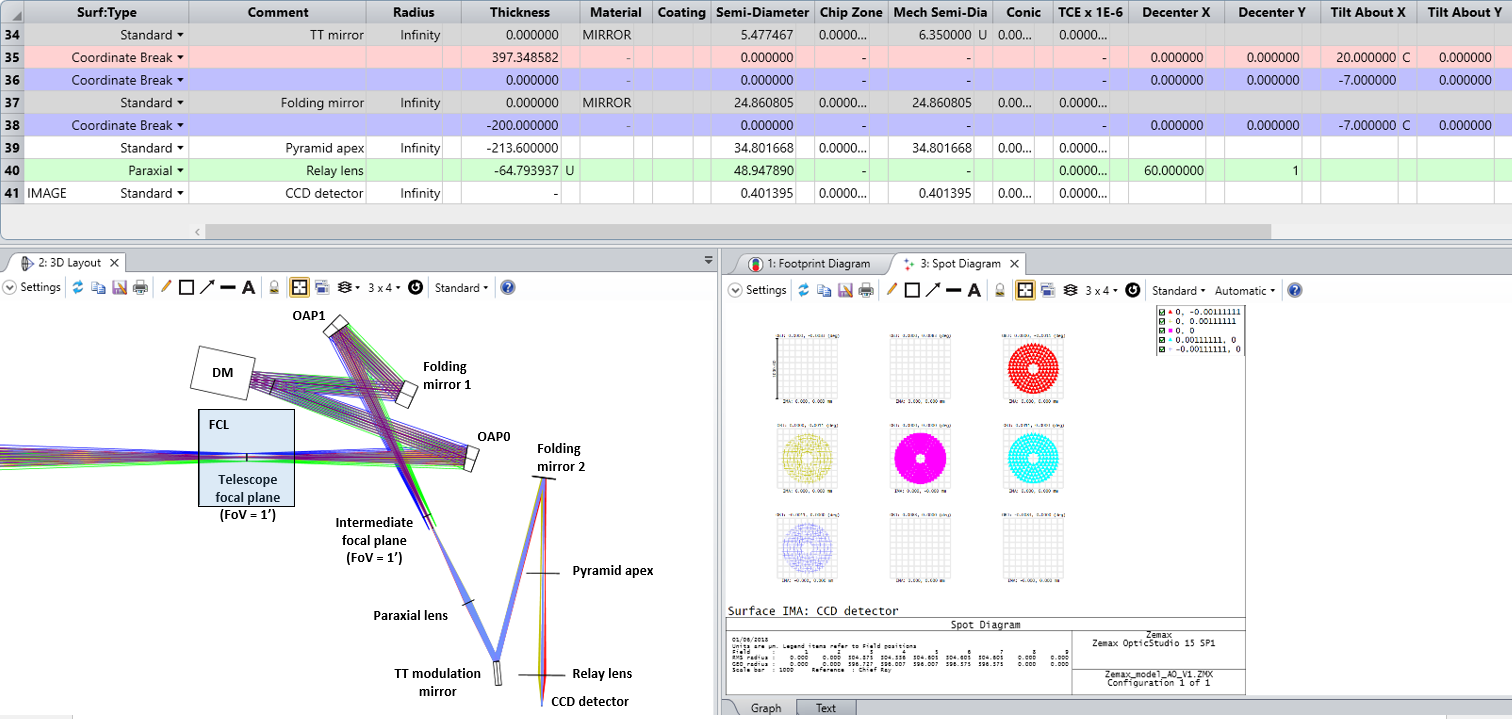
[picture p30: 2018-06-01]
20180518_AO_design_report/images/Zemax_model_FP_CCD_foldMirror.PNG

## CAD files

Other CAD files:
20180518_AO_design_report/images/sketch_ray_tracing.SLDDRW
Drawing_beam_TT.SLDDRW

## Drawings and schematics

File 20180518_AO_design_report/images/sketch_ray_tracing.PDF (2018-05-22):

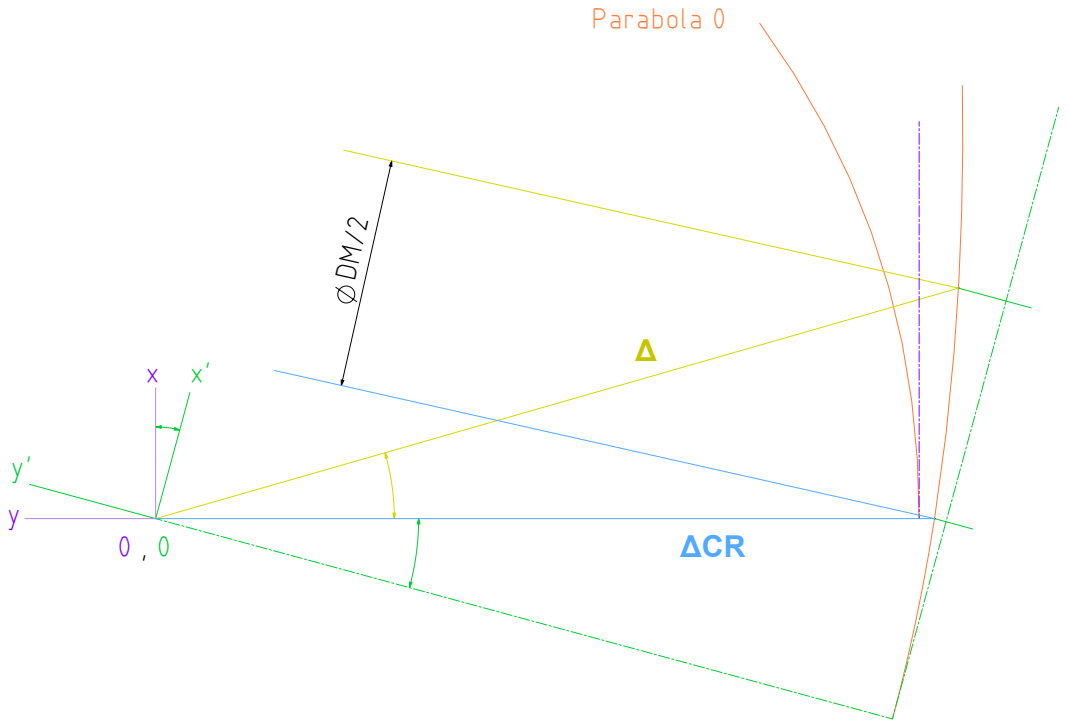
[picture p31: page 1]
Parabola 0; ΔCR; FINISH:; DEBURR AND; BREAK SHARP; DO NOT SCALE DRAWING; REVISION; SCALE:1:1; SHEET 1 OF 1

UNLESS OTHERWISE SPECIFIED:
DIMENSIONS ARE IN MILLIMETERS
SURFACE FINISH:
TOLERANCES:
LINEAR:
ANGULAR:

NAME | SIGNATURE | DATE | | | | TITLE:

DRAWN
CHK'D
APPV'D
MFG
Q.A | | | | MATERIAL: sketch_ray_tracing | DWG NO. | A0

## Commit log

2018-05-22 First version
    [sketch_ray_tracing.SLDDRW]
2018-05-22 Design up to DM
    Zemax design :
    alpha OAP0/1 = 20°, fOAP0/1 = 445mm
    Report : jusqu'au DM tilté pour compensé tilt OAP0
2018-05-24 Design up to OAP1
    Report and Zemax up to the section concerning the first folding mirror.
    emax design :
    alpha OAP0/1 = 20°, fOAP0/1 = 445mm, fold mirror 1 angle = 20°@(-250+48.03)mm du DM
2018-05-24 Design up to TT mod mirror
    Report and Zemax up to the section concerning the TT modulation mirror.
    alpha OAP0/1 = 20°, fOAP0/1 = 445mm, fold mirror 1 angle = 20°@(-250+48.03)mm du DM, choix par tatonnement de la focale et la distance au Intermediate FP pour l'OAP2 afin d'obtrenir une pupille assez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
    fOAP2 = 130mm, Distance IFP2OAP2 = 145mm
    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
2018-05-25 Design up to pyramid apex
    Report and Zemax :
    Only one lens from the intermediate FP to the TT and the apex of the pyramid.
    The option of a lens instead of OAP is good because easy and 500nm-900nm for the wavelength range on the WFS detector
    [Drawing_beam_TT.SLDDRW]
2018-05-30 Design up to the pyramid apex
    Optimization of the focal length of the lens to have a F#=60, a beam footprint on the TT modulation mirror of approx 5mm and the TT mirror tilted at 20° to allow us to insert the ADC around the pupil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
    [Drawing_beam_TT.SLDDRW]
2018-05-30 Design up to the CCD
    The Lens relay between the pyramid and the detector is designed.
    We still need to optimize the distance from the apex of the pyramid and the lens in order to have 0.792/2mm in diameter at the detector plane.
    [Drawing_beam_TT.SLDDRW]
2018-06-01 Design up to the CCD with fold mirror
    Final design of the optics bending the beam before the pyramid apex to save space.
    XYZ stage for the WFS path so place it in a movable box (shoe box)
    [Drawing_beam_TT.SLDDRW]
2018-06-06 Design with the ADC made of air and the science path
    This version contains all the optical elements needed in paraxial mode.
    The Zemax design is with 20° angle for the OAPs
    The report does not have the section explaning about the necessity or not of a field correction lens.
2018-06-07 Design using an OAP of 15deg
    I have deleted the _V2_OAP15deg version and changed the values in the V1_optimization_Model in order to have only one file updated.
    The Zemax design is complete exept for the science path.
    [Drawing_beam_TT.SLDDRW]
2018-06-19 ADC design : changes for the dispersion formula coefficients (V1)
    until now the ceffciients for the dispersion formula were taken the same for Schott and Ohara catalog (Sellmeier) or it is not true.
    Changes in the functions are done but not all
    [SellmeierCoeffOhara.csv, SellmeierCoeffSchott.csv]
2018-06-20 ADC design : changes for the dispersion formula coefficients (V2)
    Finally I saw that the dispersion coefficients are sometimes Sellmeier and sometimes not but no logic behind. I have to do again the calcul of refractive index
    [OHARA_20180518_5.xlsx, OHARA_20180518_6.xlsx, SellmeierCoeffOhara.csv, SellmeierCoeffSchott.csv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]
2018-06-20 ADC design : python script to determine the best match of glasses for the prism
    I have dowloaded catalogs updated from official websites : Ohara (update May2018 - http://www.ohara-inc.co.jp/en/product/optical/opticalglass/01009.html#04)
    Schott (update March 2017 - https://www.schott.com/advanced_optics/english/download/index.html)
    [OHARA_20180518_5.xlsx, OHARA_20180518_6.xlsx, OharaSellmeierCoefficients201805.csv, OharaSellmeierCoefficients201805.xlsx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]
2018-06-21 ADC design : python script to determine the best match of glasses in finished
    the 'glassChoice.py' and 'modelisationADCfunctions.py' are updated in order to deliver the best glass combination depending on the criteria : exit angle BDCQ minimum
    [OharaGlassProperties201703.csv, OharaSellmeierCoefficients201805.csv, SchottGlassProperties201703.csv, SchottSellmeierCoefficients201703.csv]
2018-06-21 ADC design : code and Zemax
    the code has been updated to take the real parameters for the computation of the atmospheric dispersion (RH=0.8, altitude=3170, temperature=-15°C and the total pressure is taken from python codes P= 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
    These parameters are entered in the Zemax model for the atmospheric layer and the best glasses choices are tested in Zemax. We have seen that the angle retrieved with the python code do not give good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
    ToDo : check teh angle compuattion in Python and find the reason why is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
